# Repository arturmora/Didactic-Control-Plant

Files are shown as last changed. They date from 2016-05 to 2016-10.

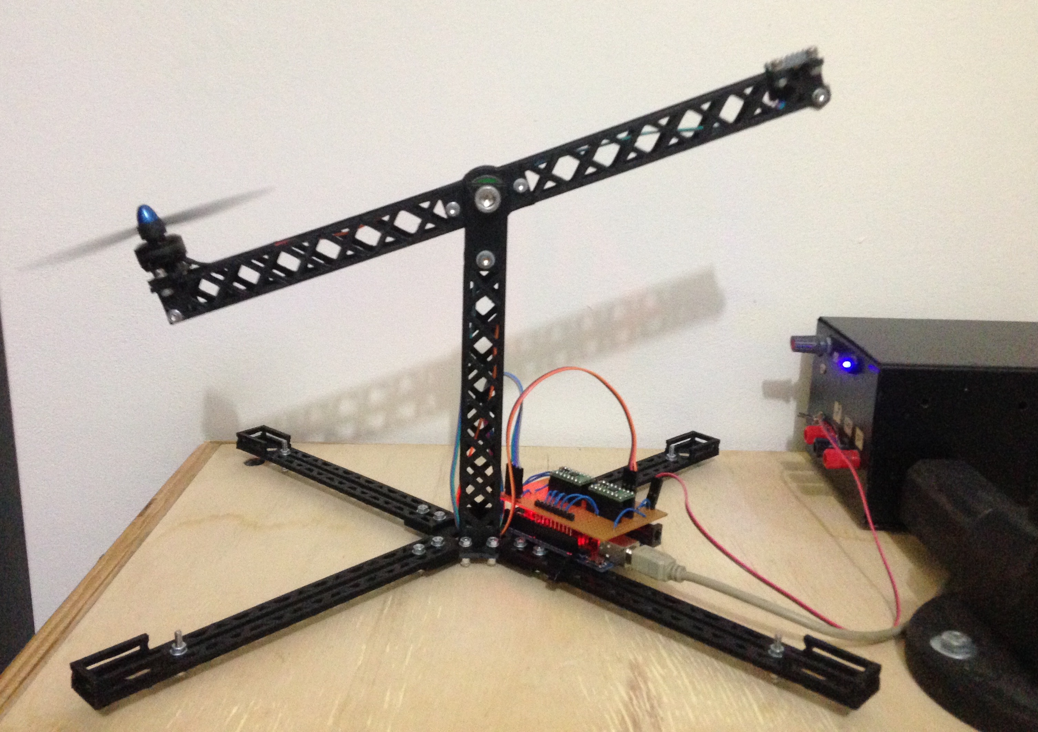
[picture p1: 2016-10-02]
Didactic Control Plant.jpeg

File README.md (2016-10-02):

# Didactic-Control-Plant 
The Didactic Control Plant is my final project for my graduate in Control and Automation Engineering, at Universidade Federal de Itajubá. You can see this job working <A href="https://youtu.be/cij42IYmPko" title="Youtube Didactic Control Plant">here</A>.
Feel free to download, share and change the code, the 3D files and the features.

To build this project, you will need:

Eletronics:
- Arduino UNO
- Shield MPU6050 (accelerometer and gyroscope)
- 2 Shields DRV8833 (or 1 ESC for your motor, but need to change the program)

Printed parts:
- 1 Frame
- 1 Adapter
- 2 Motor (1 normal and 1 mirrored)
- 2 Sensor (1 normal and 1 mirrored)
- 2 Tower
- 4 Feet

Screws, Nuts and Washers:
- 2 Screws M2 8mm
- 8 Screws M3 10mm
- 4 Screws M3 15mm
- 3 Screws M3 25mm
- 1 Screw M4 35mm
- 1 Screw M8 35mm
- 36 Nuts M3
- 2 Nuts M4
- 1 Nut M8
- 64 Washers M3
- 3 Washers M4

Others:
- 1 Motor Brushless Skyartec 1806 2200Kv (or any similar)
- 1 Propeller 5x3 (or any that fit with your motor)

Any questions, write to me: arturmora@gmail.com 
;)
By Artur Átila Moraes

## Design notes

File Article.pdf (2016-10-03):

UMA PLANTA DE CONTROLE DIDÁTICA DE UM HELICÓPTERO COM 1 DOF

Artur Átila Moraes

### Orientador: Prof. Luis H. C. Ferreira

Instituto de Engenharia de Sistemas e Tecnologia da Informação - IESTI

Resumo - Este artigo apresenta o desenvolvimento de uma planta de controle didática de um helicóptero com

### 1 grau de liberdade – Degrees of Freedom (DOF). Na

realização do projeto, foi utilizada a plataforma open source Arduino para fazer o controle PID de um motor brushless, o sensor MPU6050 para a realimentação da malha e o driver DRV8833 para substituição do ESC, assim como uma impressora 3D para prototipagem das peças, objetivando o baixo custo. Ao final, será mostrado como a planta, que possui modelo linear de segunda ordem, é estável com um overshoot de 16% e tempo de acomodação de 13s.

Palavras-Chave: Planta Didática, 1 DOF, Arduino, Controle PID, Motor Brushless, MPU6050, DRV8833, Open Source, Baixo Custo.

I. INTRODUÇÃO

Uma das formas de se estudar a teoria de controle na prática é através do uso de equipamentos laboratoriais, que permitam enxergar um controlador atuando em um problema físico concreto. A isso, é dado o nome de plantas de controle didáticas, que geralmente possuem custo elevado, restringindo o acesso livre aos alunos.
Nesse contexto, foi construída uma planta de controle didática de um helicóptero com 1 grau de liberdade, com baixo custo e material open source, a fim de disseminar conhecimento facilitando o acesso.
Esse projeto é uma continuação da iniciação científica intitulada “Uma Controladora de Motores Brushless Utilizando Eletrônica Embarcada de Baixo Custo para Navegação de Multicópteros”, desenvolvida pelo mesmo aluno e orientador deste trabalho.
Assim, esse artigo irá apresentar o desenvolvimento dessa
planta, | compartilhada | por | meio | do | link
https://github.com/arturmora/Didactic-Control-Plant.git. Para melhor entendimento do projeto, este será dividido aqui em: modelagem, mecânica, eletrônica, controlador e programação. Ao fim, serão apresentados os resultados e a conclusão deste trabalho.

II. MODELAGEM DO PROBLEMA

O modelo físico da planta consiste em uma haste horizontal de comprimento l que varia seu ângulo θ em torno de seu centro geométrico, ligado a um eixo com atrito dinâmico B. Acoplado à ponta da haste, existe um motor com hélice capaz de gerar um empuxo E. O empuxo gerado pelo motor é o produto de uma constante K pela velocidade do rotor w elevado ao quadrado e I o momento de inércia. A Figura 1 exemplica o modelo.

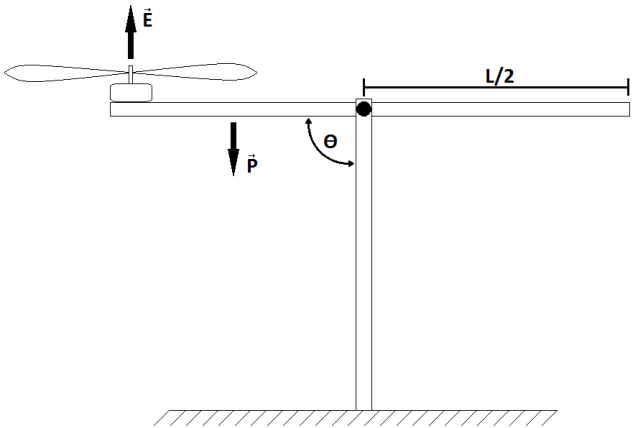
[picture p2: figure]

Fig. 1 - Modelo da Planta de um Helicóptero com 1 DOF

Esse sistema tende a ser instável já que o centro de massa está deslocado para o lado do motor. Assim, o problema de controle está em manter a haste na posição horizontal. Através de aproximações, o sistema é considerado linear e de segunda ordem [1], representado pela equação (1).

(I + m. l

2
). θ

′′ +B. θ

′ + m. l. g. sin(θ) = K. w

2
(1)

III. MECÂNICA

A estrutura mecânica foi projetada levando-se em conta três requisitos. Primeiro, o projeto da planta deveria ser open source e de fácil construção. Assim, as peças foram

UNIVERSIDADE FEDERAL DE ITAJUBÁ ENGENHARIA DE CONTROLE E AUTOMAÇÃO projetadas para serem manufaturadas em impressoras 3D Segundo, o custo deveria ser baixo, para isso a estrutura foi projetada com o mínimo possível de peças. Terceiro, para a aproximação da modelagem ser possível, o atrito entre o braço móvel e a base deveria ser baixo, portanto, foi utilizado um rolamento acoplado ao centro da haste horizontal, como pode ser visto em detalhe na Figura 2.

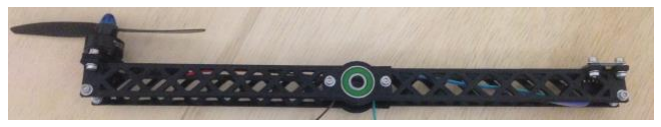
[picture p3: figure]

Fig. 2 – Haste Horizontal com Rolamento no Eixo

As peças, que foram desenhadas no software Google Sketchup, foram impressas utilizando filamento ABS, com preenchimento de 15% do tipo concentric, utilizando uma impressora 3D modelo Prusa Mendel I2, construída pelo próprio aluno. Assim, a estrutura foi montada com 12 peças impressas e com as peças descritas na Tabela 1.

Tabela 1 - Tipo e Quantidade de Peças

Peça | Quantidade
Parafuso philips M2 8mm | 2
Parafuso allen M3 10mm | 8
Parafuso allen M3 15mm | 4
Parafuso allen M3 25mm | 4
Parafuso allen M4 35mm | 1
Parafuso allen M8 35mm | 1
Porca M3 | 36
Porca M4 | 2
Porca M8 | 1
Arruela M3 | 64
Arruela M4 | 3

O braço pode variar o ângulo em 90o
, sendo o meio da
variação a posição horizontal. O comprimento da haste horizontal possui 34 cm e a vertical 18 cm.
A Figura 3 mostra a planta construída em funcionamento, com o sensor inercial acoplado na ponta direita e o motor na ponta esquerda.

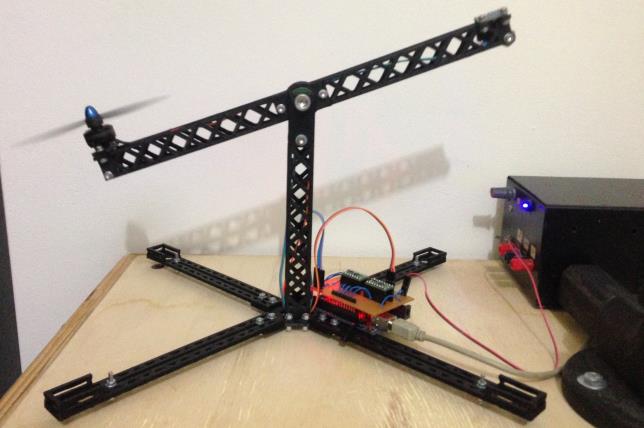
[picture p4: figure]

Fig. 3 – Planta em Funcionamento

IV. ELETRÔNICA

Alguns conhecimentos prévios são necessários para entender como a eletrônica nesse projeto funciona. Assim, algumas informações básicas sobre o motor, o sensor e o microcontrolador utilizados serão explicadas a seguir.

IV.2 Motor Brushless

O funcionamento de um motor brushless (BLDC), que na tradução livre significa “sem bucha”, é similar ao de um motor de passo. Neste, cada par de enrolamento é excitado numa dada ordem fazendo o motor girar.
O motor BLDC possui 3 fios que são ligados às bobinas. Elas são interligadas em configuração delta ou estrela.
O rotor é formado por imãs permanentes que são atraídos pelo campo magnético criado pelas bobinas do estator, assim ele é considerado de tipo síncrono.
Além disso, ele pode ser de tipo inrrunner, rotor interno ao estator, ou outrunner, rotor externo ao estator.
As vantagens do motor BLDC são sua alta eficiência, alta velocidade, longevidade, baixa manutenção, melhores características de velocidade por torque, elevada densidade de potência e baixo nível de ruídos [2].
A desvantagem está na complexidade de controle do motor, que para isso utiliza um sistema com alto custo, chamado ESC (Eletronic Speed Control).

IV.2.1 Motor Brushless Skyartec 1806

Um ponto crucial do projeto foi a escolha do motor. Este deveria ter baixo custo, baixo consumo de corrente e ser capaz de gerar empuxo suficiente para movimentar a haste. O motor escolhido foi do fabricante Skyartec, modelo 1806, que possui uma constante Kv = 2200, com consumo máximo de 8 A e uma eficiência máxima de 90% [3].
A constante Kv está relacionada à velocidade máxima de rotação de acordo com a tensão nomimal. A equação 2 mostra essa relação, sendo a tensão nominal desse motor de 3 a 12 V.
RPMmáx = Kv . Tensãomáx | (2)

A hélice recomendada para este motor possui tamanho 5x3, construída em fibra de carbono. Essa medida significa que ela tem 5 polegadas de comprimento e possui 3 polegadas de passo, que é o deslocamento a cada volta sob condições normais.

IV.2.1 Eletronic Speed Control

O ESC é responsável por comutar de forma correta as fases do motor brushless. Esse circuito contém basicamente um microcontrolador, um circuito de feedback e um circuito de potência.
O circuito de potência possui 3 meias pontes H, como mostrado na Figura 4, que podem assumir 3 estados: nível alto, nível baixo e flutuante [4]. Cada meia ponte H é conectada a uma fase do motor.

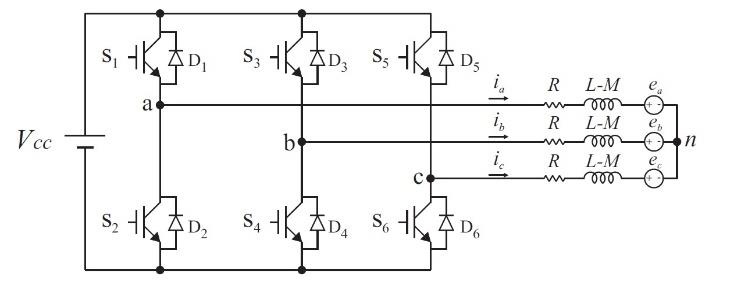
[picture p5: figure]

Fig. 4 - Circuito de Potência Simplificado

O circuito de feedback detecta a posição do rotor, através de duas técnicas. A primeira técnica é utilizada para motores com sensor, óptico ou de campo magnético (sensor Hall). Esse sensor é ativado quando um ímã passa por ele, indicando a posição do rotor. A segunda técnica é utilizada para motores tipo sensorless, na tradução livre “sem sensor”, para isso o circuito detecta a força contra-eletromotriz gerada pelo ímã permanente ao passar pela meia ponte H em estado flutuante [5].
Conhecida a posição do rotor, o microcontrolador decide o momento exato de comutar as fases, seguindo uma ordem estabelecida, mostrada na Tabela 2, que é repetida infinitamente fazendo o motor girar.

Tabela 2 – Sequência de Comutação das Fases

Fase A | Fase B | Fase C | Sequência
Alto | Flutuante | Baixo | 1
Alto | Baixo | Flutuante | 2
Flutuante | Baixo | Alto | 3
Baixo | Flutuante | Alto | 4
Baixo | Alto | Flutuante | 5
Flutuante | Alto | Baixo | 6

A velocidade do motor é determinada pelo tempo entre a troca de estados, sendo que quanto menor o tempo, mais rápido o motor.

IV.3 MPU6050

O MPU6050 é um shield composto por dois sensores inerciais, o acelerômetro e o giroscópio [6], que juntos são responsáveis pela realimentação da malha de controle do sistema, informando ao microcontrolador qual a orientação angular do sensor. Neste caso, a orientação angular da haste.
O giroscópio mede a velocidade angular de um objeto. Assim, quando o sensor está parado, ele fornecerá valores nulos. Quando em movimento, fornecerá valores positivos ou negativos, dependendo do sentido de rotação do giroscópio.
O acelerômetro mede a força de aceleração aplicada ao sensor, sendo essas forças compostas por forças estáticas, a própria aceleração da gravidade, e forças dinâmicas, quando o sensor sofre alguma força de outra natureza.
O shield também possui um processador de movimento embarcado (DMP) capaz de fazer a fusão sensorial e filtrar os dados.

IV.4 DRV8833

O shield DRV8833, da marca Pololu, é basicamente um driver com duas pontes H capaz de fornecer até 1,2 A por canal, trabalhando numa faixa de 2,7 V a 10,8 V [7]. Neste projeto, apenas um lado da ponte é acionado pelo Arduino, logo, ao deixar o outro lado desconectado, a ponte H se comporta como meia ponte. Por serem necessárias 3 meias pontes para acionar o motor, foram utilizados dois shields.
Apesar da corrente máxima suportada pelo driver ser inferior ao consumo máximo do motor brushless, eles foram utilizados no lugar do ESC por possuírem menor custo, já que nessa condição o empuxo gerado é suficiente para movimentar a haste da estrutura.

IV.5 Arduino

Nesse projeto, existe a necessidade de interpretar os dados gerados pelo sensor, verificar a velocidade atual do motor e, com base num controlador PID, decidir se a velocidade deve aumentar ou diminuir no intuito de controlar a planta. Essas funções são realizadas pelo Arduino, um microncontrolador altamente difundido no mundo acadêmico, devido ao seu baixo custo e por ser uma plataforma de software e hardware open source. Portanto, foi utilizada a placa Arduino UNO que opera numa frequência de 16 MHz, possui 14 portas digitais e 6 portas analógicas. Além disso, o shield MPU6050 e o shield DRV8833 são compatíveis com o microcontrolador.

IV.5 Esquema de Ligação

Após a escolha de todos os componentes, foi criado um esquema de ligação, representado pela Figura 5, que consiste em conectar os circuitos de acordo com as especificações do fabricante encontradas em seus respectivos datasheets.

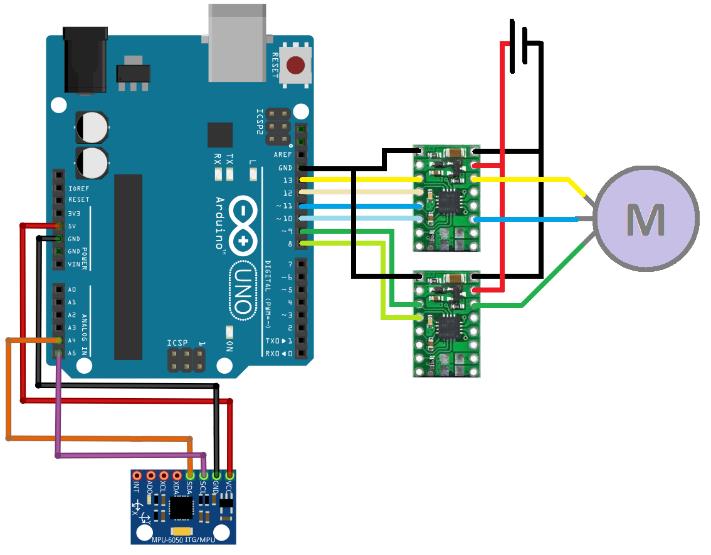
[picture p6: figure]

Fig. 5 – Esquemático de Ligação

Os componentes foram conectados e testados utilizando um protoboard. Em sequência, os componentes foram soldados sobre uma placa de cobre perfurada, comum em projetos de prototipagem rápida, utilizando jumpers feitos de fio, no lugar das trihas. Para minimizar peças soltas, a placa foi dimensionada para encaixar sobre o Arduino Uno, como pode ser visto na Figura 6.

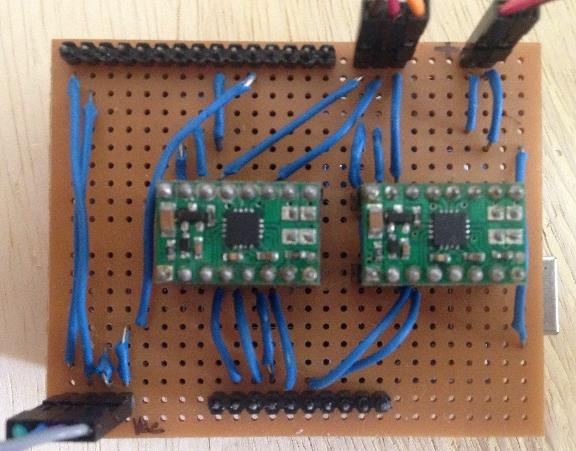
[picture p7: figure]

Fig. 6 – Circuito Encaixado no Arduino Uno

V. CONTROLADOR

O modelo do sistema consiste em uma equação de segunda ordem que pode ser linearizada, como mostrado anteriormente. Desse modo, através da biblioteca PID do Arduino, foi implementado um controlador proporcional-integrativo-derivativo, descrito pela equação (3), capaz de levar o sistema a estabilidade [7].

C(s) = Kp +

Ki
s
+ Kd. s | (3)

VI. PROGRAMAÇÃO

Considerando que a planta se encontra inicialmente em repouso e com o motor desligado, a haste estará em seu
ponto mais baixo, numa inclinação de -45o | em relação ao
plano horizontal. Assim, existem duas situações diferentes a serem controladas.

VI.1 Inicialização

O acionamento correto do motor depende de parâmetros que são definidos no cabeçalho do programa:
- Velocidade mínima e máxima de rotação;
- Velocidade de start do motor;
- Portas de saída para acionamento do driver DRV8833;
- Ângulo mínimo e máximo da haste;
- Offset do shield MPU6050;
- Set point do controlador;
- Ganhos Kp, Ki e Kd;
- Tempo de amostragem.
Além desses parâmetros, o programa necessita das seguintes bibliotecas: controlador (PID_v1.h), interrupção (TimerOne.h), comunicação I2C (I2Cdev.h) e sensor MPU6050 (MPU6050_6Axis_MotionApps20.h).
Após o cabeçalho, o programa entra numa rotina de partida do motor até atingir uma rotação mínima. Em seguida, o sensor é ativado e o controlador é colocado em modo automático, para se fechar a malha do sistema.

VI.1 Controle

A rotina de controle repete infinitamente as funções:
- Ler novo valor do sensor;
- Calcular velocidade do motor;
- Atualizar velocidade do motor.
O cálculo da velocidade leva em consideração a diferença entre o set point e o valor lido pelo sensor. Caso esteja abaixo ou acima do set point, a velocidade aumenta ou diminui, respectivamente, de acordo com o valor calculado pela função do controlador PID.
Em paralelo, uma função que troca o estado do circuito de potência para girar o motor, de acordo com a Tabela 2, é chamada através de uma interrupção temporal.
O tempo que determina a ocrrência da interrupção é determinado por uma função de mapeamento, que converte a saída do PID, que varia de 0 a 255, em tempo entre as comutações, que varia de 350 µs e 500 µs.
Como o microcontrolador não conhece a posição do rotor, uma função que compara o tempo de comutação anterior com o novo limita a aceleração, para não ocorrer a perda de sincronia entre as comutações e a posição real do motor. Portanto, a velocidade obedece uma função rampa, que altera em 1µs o tempo de comutação a cada rotina completa.

VII. RESULTADOS E ANÁLISES

O controle em malha fechada do sistema inicia após o motor atingir uma velocidade de 3333 RPM. Assim, a velocidade do motor em RPM, que é a entrada do sistema, é manipulada por um controlador PID com ganhos Kp = 1, Ki = 1 e Kd = 4, utilizando um tempo de amostragem de 30 ms. A Figura 7 apresenta esse controle, sendo o instante zero o momento de fechamento da malha.

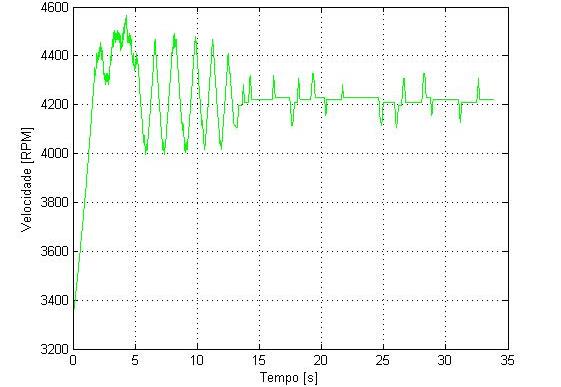
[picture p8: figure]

Fig. 7 – Gráfico da Entrada

Os ganhos foram sintonizados de forma empírica, escolhendo um valor de Kp para qual o sistema tivessse um overshoot de até 50%, em seguida foi adicionada a parte derivativa aumentando-a até o overshoot ficar abaixo de 20% e por fim foi adicionado a parte integrativa para zerar o erro em regime permanente. A Figura 8 mostra a resposta do sistema, representada em graus, que representa a posição da haste horizontal em relação a vertical. O set point de 0o
indica a haste posicionada horizonalmente.

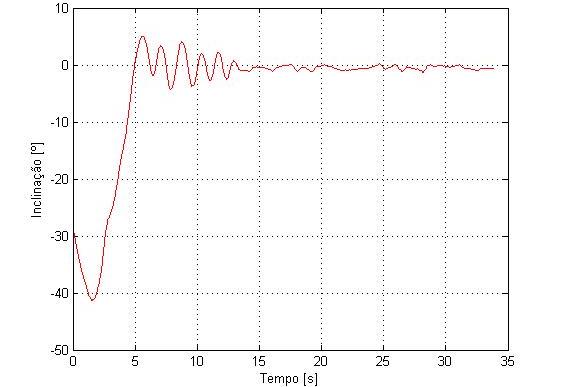
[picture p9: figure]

Fig. 8 – Gráfico da Saída

Foi obtido um overshoot de 16% e tempo de acomodação de 13s. A variação negativa no início do gráfico é devido a um erro de acomodação na inicialização do sensor.
O sistema é estável na presença de distúrbios, garantindo um controle robusto. Isso foi verificado criando um distúrbio no lado direito da haste, batendo nela com a mão para cima e para baixo, como mostra a Figura 9.

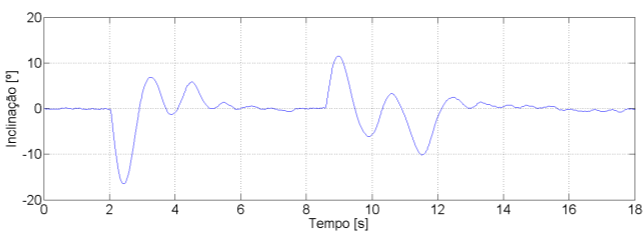
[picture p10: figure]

Fig. 9 – Gráfico da Saída com Distúrbio

Algumas vezes, pelo fato da técnica utilizada para rotacionar o motor não utilizar a localização da posição do rotor, o campo girante perde a sincronia com o rotor, parando o funcionamento do sistema.
O custo estimado do projeto foi de R$147,00. Sendo R$15,00 em parafusos; R$15,00 do sensor MPU6050, R$40,00 do motor, R$12,00 da hélice, R$15,00 do Arduino, R$40,00 do driver e R$10,00 em fios e filamento.

VIII. CONCLUSÃO

Este trabalho final de graduação tinha como objetivo principal o desenvolvimento de uma planta na qual pudesse ser utilizada uma técnica de controle. Como foi possível utilizar o controlador PID, o objetivo foi alcançado. Outro objetivo era desenvolver um projeto open source, de baixo custo e fácil construção, trazendo a possibilidade de que outros alunos construam a planta didática a fim de estudar o controlador PID ou implementar outras ténicas de controle.

O aluno pôde se aprofundar em diferentes áreas da engenharia, como a mecânica, a eletrônica e a programação, mas também teve a oportunidade de utilizar os conceitos aprendidos durante a graduação. Além de
desenvolver | habilidades | voltadas | para | o
empreendedorismo, como planejamento de um projeto. Em trabalhos futuros poderá ser feita a identificação do sistema através de ensaios em malha aberta, para a modelagem do sistema. Além disso, é possível fazer a adição de mais um grau de liberdade, adicionar a técnica de localização do rotor e desenvolver uma interface gráfica, assim, o aluno poderia alterar os valores das constantes do controlador PID e gerar gráficos de entrada e saída do sistema em tempo real.

IX. AGRADECIMENTOS

Primeiramente agradeço a minha família, a minha namorada e aos meus amigos, que me deram apoio para continuar acreditando e carinho para sentir que vale a pena. Agradeço também aos meus professores e toda a comunidade open source que dividem o conhecimento, sabendo que só assim teremos um futuro melhor. Finalmente agradeço ao meu orientador e ao grupo de microeletrônica, que me acolheram desde o início da faculdade, sempre me orientando, tornando esse TFG e outras conquistas possíveis.

X. REFERÊNCIAS
[1] K. Ogata e Y. Yang – “Modern control engineering”, Prentice-Hall Englewood Cliffs, NJ, 1970.
[2] P. Yedamale - “Brushless DC (BLDC) Motor Fundamentals”, Microchip, 2003.
[3] Skyartec – “1806 Brushless Motor (2200Kv CW)”.
[4] D. Arrigo - “L6234 Three Phase Motor Driver”, STMicroeletronics, Abril, 2001.
[5] W. Brown - “Brushless DC Motor Control Made Easy”, Microchip, 2002.
[6] Invensense – “Mpu-6000 and mpu-6050 register map and descriptions”, 2012.
[7] Texas Instruments – “Dual H-Bridge Motor Driver”, 2013.

BIOGRAFIA:

Artur Átila Moraes
Nasceu em São Paulo (SP), em 1992. Estudou em São Caetano do sul, tendo recebido o título de Técnico em
Eletrônica | na | Escola | Técnica
Estadual Jorge Street. Ingressou na UNIFEI em 2011, no curso de
| Engenharia | de | Controle | e
Automação, onde realizou duas iniciações científicas como bolsista do CNPq. Estagiou na RZX Tecnologia, por 6 meses, desenvolvendo um sensor utilizado na área de óleo e gás. Em 2015, ganhou o concurso “Internet of Cows”, da BovControl, para desenvolver um sensor wearable com futuro registro de patente.

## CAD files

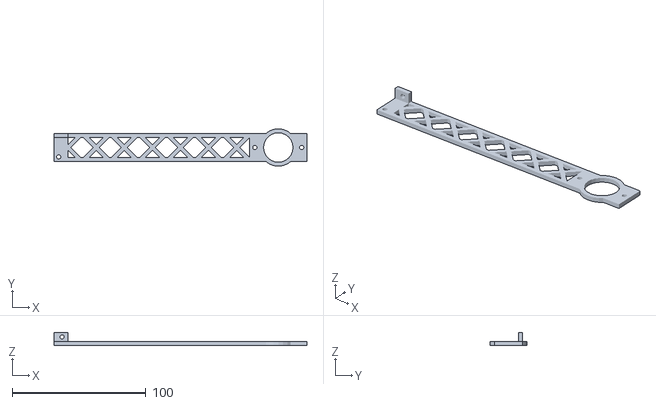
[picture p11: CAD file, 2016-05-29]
Motor.stl
189.0 x 28.0 x 10.0

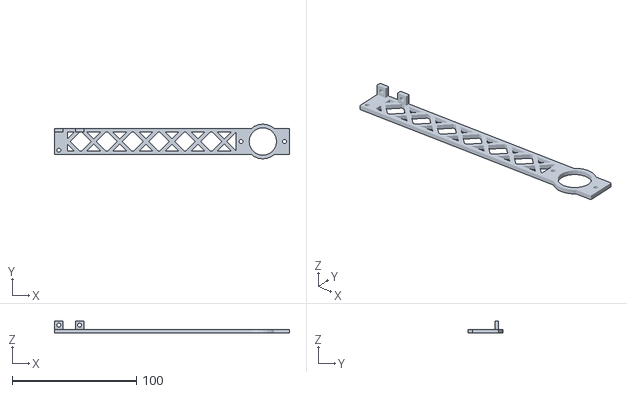
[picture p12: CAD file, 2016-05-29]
Sensor.stl
189.0 x 28.0 x 10.0

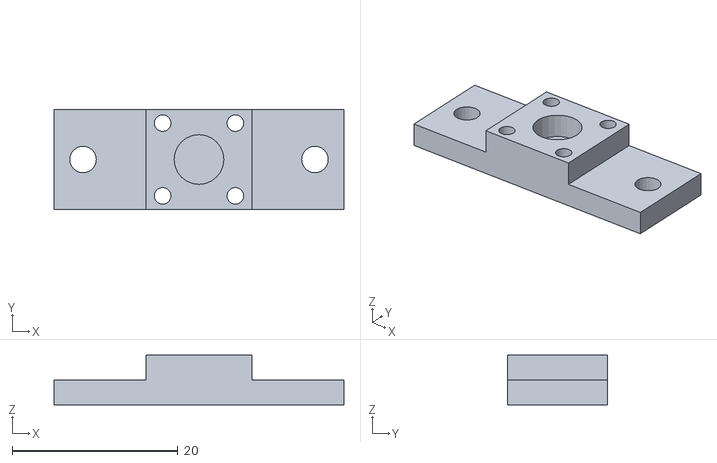
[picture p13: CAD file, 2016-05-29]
Adapter.stl
35.0 x 12.0 x 6.00

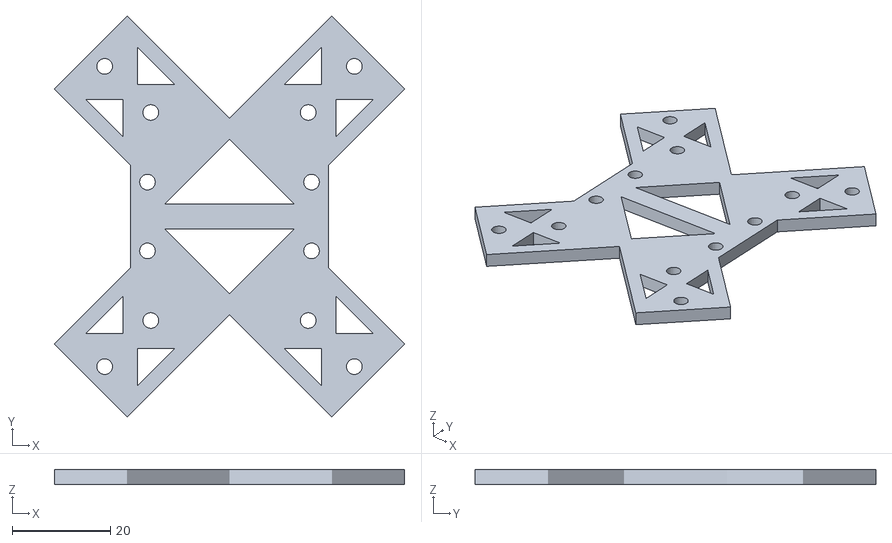
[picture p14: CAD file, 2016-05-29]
Frame.stl
71.3 x 81.6 x 3.00

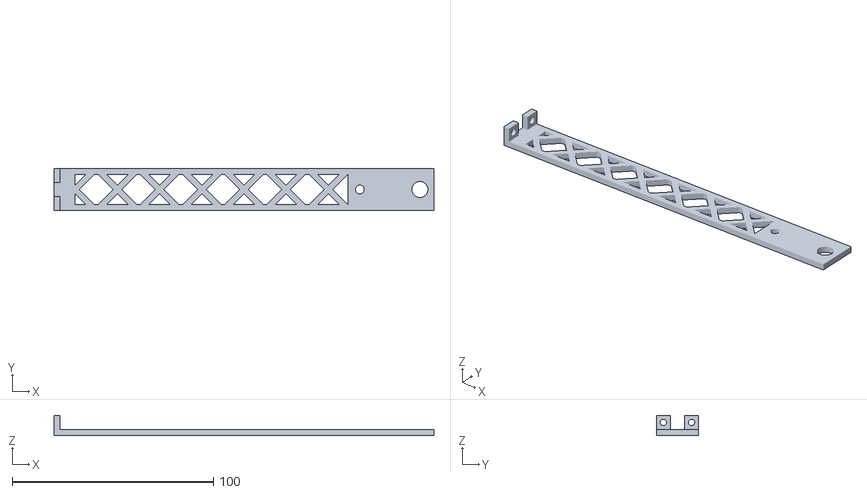
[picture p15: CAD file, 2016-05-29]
Tower.stl
189.0 x 21.0 x 10.0

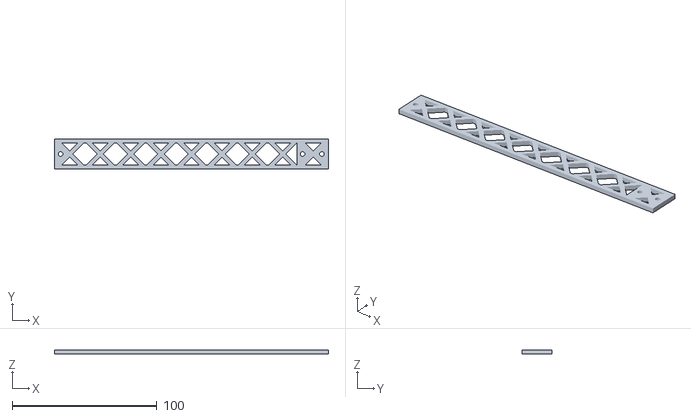
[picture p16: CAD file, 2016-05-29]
Feet.stl
189.0 x 21.0 x 3.00

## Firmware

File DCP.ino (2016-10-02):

//Autor: Artur Átila Moraes
//Esse código é utilizado para controle de uma planta didática de um helicóptero com 1 grau de liberdade.

//Declarações referentes ao BLDC
#define KV      17640           //Velocidade máxima em Kv (RPM = Kv x Volts)
#define A1      12              //A1 controla saída Aout1 no driver
#define A2      13              //A2 controla saída Aout2 no driver
#define B1      11              //B1 controla saída Bout1 no driver
#define B2      10              //B2 controla saída Bout2 no driver
#define C1      8               //C1 controla saída Cout1 no driver
#define C2      9               //C2 controla saída Cout2 no driver
#define VALMIN  350             //Intervalo mínimo para troca de estado
#define VALMAX  500             //Intervalo máximo para troca de estado
#define START   5400            //Intervalo mínimo para iniciar o motor

double val;                     //Val modifica período da saída
double rotation = VALMAX;       //Velocidade de rotação
unsigned long startTime = 0;
volatile int aux = 1;

#include "TimerOne.h"

//Declarações referente ao MPU6050
#define ROLLMIN -22             //Menor leitura do sensor
#define ROLLMAX 23              //Maior leitura do sensor
#define XOFFSET 32              //Offset giroscópio X
#define YOFFSET 16              //Offset giroscópio Y
#define ZOFFSET -21             //Offset giroscópio Z
#define AOFFSET 5035            //Offset acelerômetro

double pitch = 0;               //Variável que recebe inclinação do sensor
uint16_t packetSize;            //Expected DMP packet size (default is 42 bytes)
uint16_t fifoCount;             //Count of all bytes currently in FIFO
uint8_t fifoBuffer[64];         //FIFO storage buffer
float ypr[3];                   //[yaw, pitch, roll] yaw/pitch/roll container and gravity vector

#include "I2Cdev.h"
#include "MPU6050_6Axis_MotionApps20.h"
MPU6050 mpu;
Quaternion q;                   //[w, x, y, z] quaternion container
VectorFloat gravity;            //[x, y, z] gravity vector

//Declarações referentes ao PID
#define KP  1                   //Constante Kp para controle
#define KI  1                   //Constante Ki para controle
#define KD  4                   //Constante Kd para controle
#define SP  525                 //Valor de SetPoint para referência
#define SAMPLE 30               //Tempo de amostragem em ms do PID

double setpoint = SP;

#include <PID_v1.h>
PID myPID(&pitch, &rotation, &setpoint, KP, KI, KD, REVERSE);

void setup() { 
  pinMode(A1, OUTPUT);
  pinMode(A2, OUTPUT);
  pinMode(B1, OUTPUT);
  pinMode(B2, OUTPUT);
  pinMode(C1, OUTPUT);
  pinMode(C2, OUTPUT);

  Timer1.initialize(START);
  Timer1.attachInterrupt(Turning);

  for(val = START; val > VALMAX*4; val -= 2){
    delayMicroseconds(val);
    Timer1.setPeriod(val);
  }
  for(val = val; val > VALMAX; val --){
    delayMicroseconds(val);
    Timer1.setPeriod(val);
  }
 
  myPID.SetMode(AUTOMATIC);
  myPID.SetSampleTime(SAMPLE);
  myPID.SetOutputLimits(VALMIN, VALMAX);
 
  Wire.begin();
  TWBR = 24;
  mpu.initialize();
  mpu.testConnection();
  mpu.dmpInitialize();
  mpu.setXGyroOffset(XOFFSET);
  mpu.setYGyroOffset(YOFFSET);
  mpu.setZGyroOffset(ZOFFSET);
  mpu.setZAccelOffset(AOFFSET);
  mpu.setYAccelOffset(-3064);
  mpu.setZAccelOffset(-303);
  mpu.setDMPEnabled(true);
  packetSize = mpu.dmpGetFIFOPacketSize();

  Serial.begin(115200);
}

void loop() {
  fifoCount = mpu.getFIFOCount();
  while (fifoCount < packetSize) fifoCount = mpu.getFIFOCount();
  mpu.getFIFOBytes(fifoBuffer, packetSize);
  fifoCount -= packetSize;
  mpu.dmpGetQuaternion(&q, fifoBuffer);
  mpu.dmpGetGravity(&gravity, &q);
  mpu.dmpGetYawPitchRoll(ypr, &q, &gravity);
  
  pitch = ypr[2]*180/M_PI;
  Serial.print(pitch);
  pitch = map(pitch, ROLLMIN, ROLLMAX, 0, 1023);
  myPID.Compute();
  Serial.print("\t");

  if( rotation > val) val ++;
  if( rotation < val) val --; 
  Timer1.setPeriod(val); 
  Serial.println(val);
}

void Turning(){
  switch(aux){
    case 1:
      digitalWrite(B1, LOW);                   
      digitalWrite(A1, HIGH);
      aux ++;
      break;
    case 2:
      digitalWrite(C2, LOW);
      digitalWrite(B2, HIGH);
      aux ++;
      break;
    case 3:
      digitalWrite(A1, LOW);
      digitalWrite(C1, HIGH);
      aux ++;
      break;
    case 4:
      digitalWrite(B2, LOW);
      digitalWrite(A2, HIGH);
      aux ++;
      break;
    case 5:
      digitalWrite(C1, LOW);
      digitalWrite(B1, HIGH);
      aux ++;
      break;
    case 6:
      digitalWrite(A2, LOW);
      digitalWrite(C2, HIGH);
      aux = 1;
      break;
  }
}
